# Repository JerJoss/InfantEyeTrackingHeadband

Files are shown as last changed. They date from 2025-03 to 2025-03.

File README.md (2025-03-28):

While most studies analyzing infant visual attention use methods varying from annotations of videos from head-mounted cameras, to fixed screen-based eye-tracking setups, increasing interest has been shown towards solutions that would pair the precision of eye-tracking with the free mobility offered by video annotation. This would allow infant research to gather high-quality visual attention data in naturalistic situations, which might yield results more representative of real-world infant environments. For this purpose, various forms of portable eye-tracking devices have been developed and used to study infant cognition, along with frequently time-consuming infant-adapted calibration procedures. Recently, the advent of calibration-free lightweight wearable eye-tracking systems developed by Pupil Labs© is offering new and simpler ways to study infant visual attention with the advantages of deep-learning calibration and miniaturization. However, despite a wide variety of wearing accessories being offered by the company, no suitable option currently exists for infants younger than 2 years old. In this paper, instructions will be provided to build a new wearing accessory for Pupil Labs’ Neon eye-tracking module adapted to 3 to 24 months-old infants, along with usage instructions.

Keywords—infant research, eye-tracking, Pupil Labs, Neon, calibration-free eye-tracking

<p>Video demonstrations:<br>
https://youtu.be/ldanZW603Fs - https://youtu.be/75sW56sUcog - https://youtu.be/vj5wvd1JuIk - https://youtu.be/4lynIBO4ydA</p>
<p>DISCLAIMER:<br>
These videos are intended solely for academic and research purposes. All content herein is shared in the context of scholarly inquiry and is not to be copied, distributed, or used for any commercial or non-research-related purpose. Unauthorized use, reproduction, or dissemination of this material is strictly prohibited.</p>

<p>Mail:<br>
jeremie.josse@univ-grenoble-alpes.fr<br></p>

<p>Files:<br>
Infant headband for Pupil Labs' Neon eyetracker — Instructions and method.pdf — Jérémie Josse (1)<br>
Custom_Neon_Module_receptacle.STL — 3D modelling by Eric Guinet (1) and Guillaume Bonnet<br>
<br>
(1) Laboratoire de Psychologie et Neuro-Cognition - UMR 5105 CNRS</p>

Thank you to Pupil Labs© for their willingness to be open source and their kind permission to make this custom use of their product public.

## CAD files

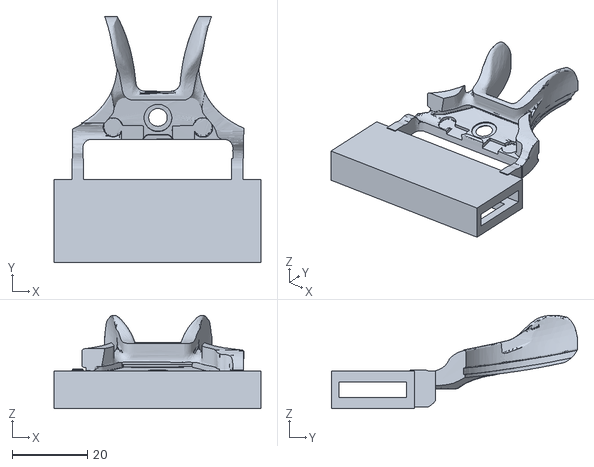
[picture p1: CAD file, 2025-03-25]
Custom_Neon_Module_receptacle.STL
55.0 x 65.4 x 24.7

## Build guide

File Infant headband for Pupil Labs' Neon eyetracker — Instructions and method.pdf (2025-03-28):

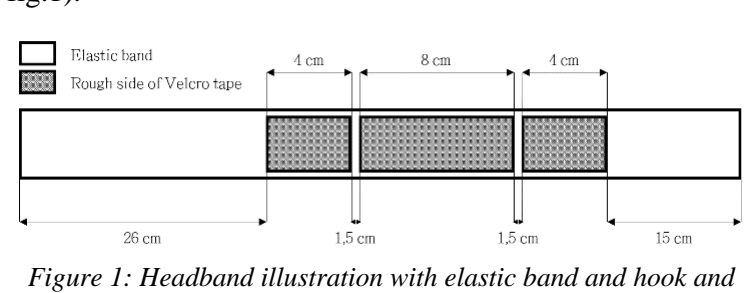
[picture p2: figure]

1 - https://github.com/JerJoss/InfantEyeTrackingHeadband/blob/main/Custom_Neon_Module_receptacle.STL 2 - https://github.com/pupil-labs/neon-geometry
3 - https://pupil-labs.com/products/neon/shop#bare-metal

# Using Pupil Labs’ Neon eye-tracking module for infants aged 3 to 24 months

Josse, Jérémie
BabyLab – Laboratory of Psychology and NeuroCognition
Grenoble Alpes University
Grenoble, France
jeremie.josse@univ-grenoble-alpes.fr

Abstract—While most studies analyzing infant visual attention use methods varying from annotations of videos from head-mounted cameras [1], [2], [4], [5] to fixed screen-based eye-tracking setups [6], [7], [8], [9], [10], increasing interest has been shown towards solutions that would pair the precision of eye-tracking with the free mobility offered by video annotation. This would allow infant research to gather high-quality visual attention data in naturalistic situations, which might yield results more representative of real-world infant environments [11]. For this purpose, various forms of portable eye-tracking devices have been developed and used to study infant cognition [3], [12], [13], [14], along with frequently time-consuming infant-adapted calibration procedures. Recently, the advent of calibration-free lightweight wearable eye-tracking systems developed by Pupil Labs© is offering new and simpler ways to study infant visual attention with the advantages of deep-learning calibration and miniaturization. However, despite a wide variety of wearing accessories being offered by the company, no suitable option currently exists for infants younger than 2 years old. In this paper, instructions will be provided to build a new wearing accessory for Pupil Labs’ Neon eye-tracking module adapted to 3 to 24 months-old infants, along with usage instructions.

Keywords—infant research, eye-tracking, Pupil Labs, Neon, calibration-free eye-tracking

I. INTRODUCTION
This document provides a series of instructions on how to make and use an accessory meant to facilitate the usage of Pupil Labs’ Neon eye-tracking module with infants aged 3 to 24 months. This eye-tracking module is particularly useful in the context of infant development research, as it is lightweight and miniaturised, and uses a deep-learning powered calibration which automatically adapts to its user — avoiding time-consuming calibration processes which might be difficult for infants to complete. In the initial phases of our experimentation with this tool, we tested various ways of using Pupil Labs’ official child-adapted frames designed for children aged 2 and older. However, due to their size and shape, we were not successful in adapting these to infant users. This led to the development of a new wearing accessory aimed towards infant wearers, which we have successfully been using to gather eye-tracking data from infants aged 3 to 24 months. We currently have an acceptance rate of 74% (n=70, aged 3 to 12m) using this tool in laboratory conditions, and 94% (n=18, aged 4 to 14m) in nurseries. Among the acceptance group, 39% have been excluded from our study due to experimental error (i.e. badly positioned module resulting in low-quality calibration, unplanned distraction in infant’s environment etc). In our whole sample of infants tested, 56% are currently included.

II. MAKING THE ACCESSORY

A. Materials
- A wide flat elastic band.
Here we used a 40mm-wide elastic band for sewing, generally used for tightening waistbands.
- Adhesive hook and loop (Velcro) strip tape.
35mm-wide.
- A plastic adjustment buckle.
- A 3D printed receptacle for the Neon eye-tracking module¹
, adapted from Pupil Labs’ open source “Just act natural” frame geometry²
- A piece of thick and soft fabric to smooth out the plastic edges.
- Pupil Labs’ Bare metal bundle: Neon eye-tracking module + Nest PCB + Android device³
B. Assembly
Cut a 60cm-long piece of the elastic band and sew 3 pieces of the rough (hook) side of the hook and loop strip tape (see fig.1).

Insert both edges of the elastic band in the adjustment buckle and sew one of the edges in a closed loop.

Cut a thin strip of the adhesive hook and loop tape, stick both sides together and form a loop around the side of the buckle. This will be used to assure the Neon eye-tracking module’s wire remains towards the back of the infant’s head so as not to distract them.

Figure 1: Headband illustration with elastic band and hook and loop strip tape dimensions.

Video demonstrations:
https://youtu.be/ldanZW603Fs - https://youtu.be/75sW56sUcog - https://youtu.be/vj5wvd1JuIk - https://youtu.be/4lynIBO4ydA

DISCLAIMER: These videos are intended solely for academic and research purposes. All content herein is shared in the context of scholarly inquiry and is not to be copied, distributed, or used for any commercial or non-research-related purpose. Unauthorized use, reproduction, or dissemination of this material is strictly prohibited.

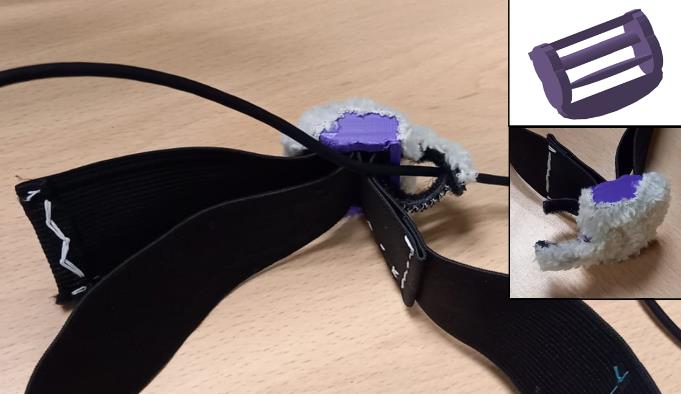
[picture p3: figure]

Glue a piece of the thick soft fabric over the buckle and the wire loop. This will make these surfaces softer in case of contact with the infant’s skin, and will decrease other problems such as the plastic or the loop getting caught in the fabric of the parents’ clothing when the infant sit on the parent’s lap (see fig.2).

Glue a piece of the thick soft fabric on the upper front section of the 3D printed module receptacle, along with some optional decorations. And glue a piece of the soft (loop) side of the hook and loop strip tape on the upper back section of the receptacle.

Screw the nest PCB inside the receptacle. Optionally, strengthen the base of the wire with a heat-shrink sleeve and small wire. This was added after an infant pulled on the wire, breaking the soldering connecting it to the nest PCB (see fig.3).

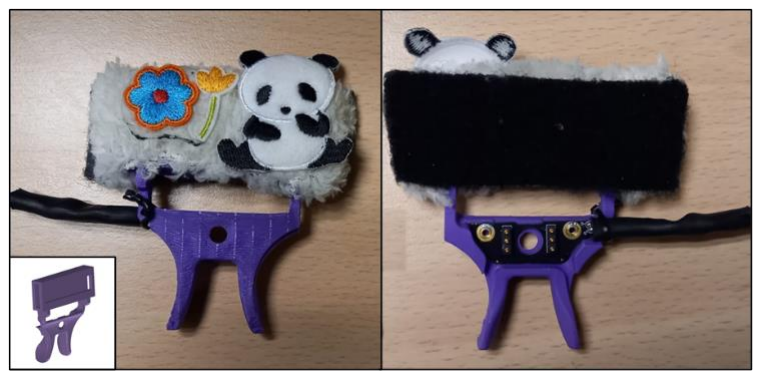
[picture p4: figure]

Screw the Neon eye-tracking module on the nest PCB and into the 3D-printed receptacle (see fig.4).

The final result should look like figure 5, with the receptacle fixed to the front of the headband using the hook and loop surfaces, and the wire going through the back loop.

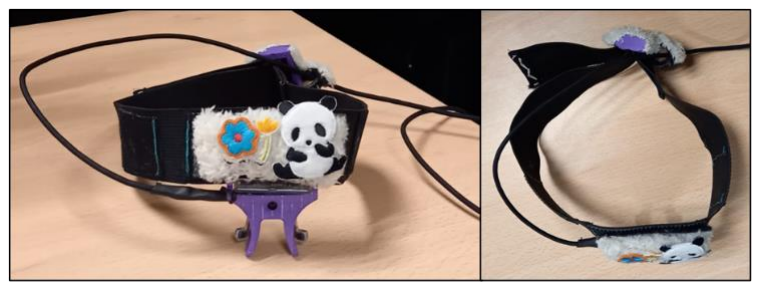
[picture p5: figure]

III. PROCEDURE
During our studies, the infant is seated on their parent’s lap, facing the experimenter. The infant is given a plush-toy meant to reassure and to distract its attention while the experimenter fits the headband and the eye-tracking module on its head. If possible, a second experimenter is present to play with the infant during the procedure.

After a short moment of playing and engaging with the infant, the first experiment takes the headband without the eye-tracking module, and approximately adjusts its circumference to be slightly wider than the infant’s head’s. At this stage, if the infant is showing more curiosity towards the headband than towards the plush-toy, it is encouraged to manipulate and familiarize itself with it. The experimenter then carefully slips the headband on the infant’s head, with the buckle to the back of the head and the rough (hook) side of the hook and loop strip tape to the front. The headband should run through the middle of the infant’s forehead. Ideally, any adjustments to its position should be done at this point while the eye-tracking module is not yet attached. If necessary, the experimenter then tightens the headband by pulling on the elastic band extending out of the buckle. Playing and engaging with the infant then continues until it seems comfortable wearing the headband.

The next step will to be to attach the eye-tracking module to the infant’s headband. Before starting, the eye-tracking module should be connected to the Android device and have been detected by the Neon Companion App. Inside the app, enable the sensor module camera view and position the Android device in a location that will be visually accessible while attaching the eye-tracking module to the infant’s headband (i.e. the parent’s chair’s armrest). Lastly, open the small loop next to the buckle and close it around the eye-tracking module’s wire, leaving just the right length for the module to reach the infant’s forehead. This will ensure that the wire won’t disturb the infant, or distract him by entering in its field of vision.

At this point, the eye-tracking module should be held above the infant’s head. The main or the second experimenter should then attempt to catch the infant’s attention. Whenever the infant’s head appears to be still, the

Figure 2: Picture of the buckle at the back of the headband.

Figure 3: Picture of the 3D-printed eye-tracking module receptacle, to be attached to the front of the headband using Velcro, along with a nest PCB.

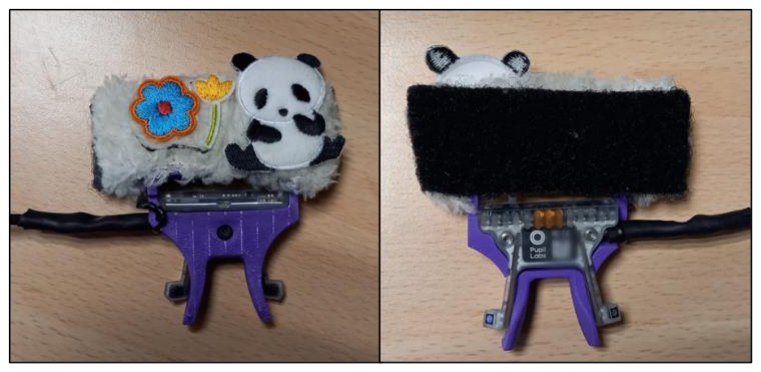
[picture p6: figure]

Figure 4: Picture of the 3D-printed eye-tracking module receptacle, to be attached to the front of the headband using Velcro, along with a Neon eye-tracking module.

Figure 5: Picture of the fully assembled headband.

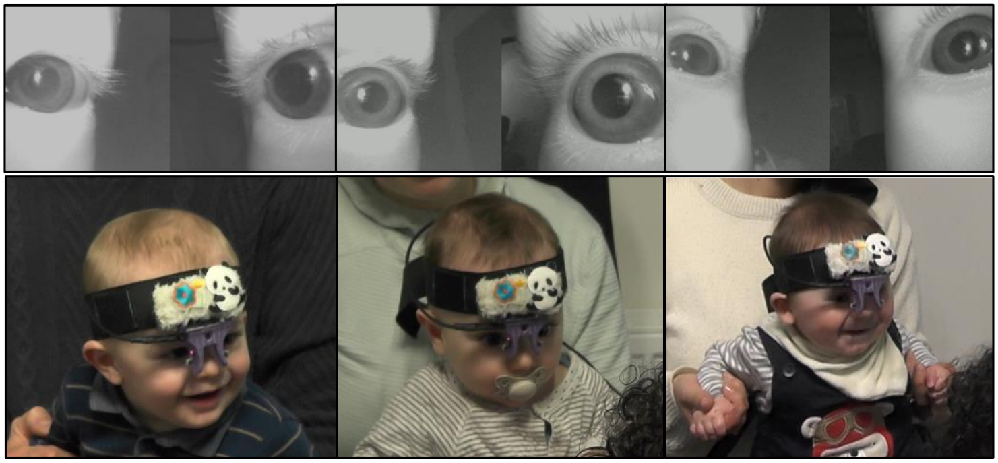
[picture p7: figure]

main experimenter attaches the eye-tracking module receptacle to the hook and loop surface on the headband. The sensor module camera view from the Neon Companion App should be visible during this process, and be used as a positioning guide for the experimenter. Once positioned, both eyes should be visible in the feedback (see fig.6). Ideally, the eyes should be well centered along the vertical axis of the visual feedback (as in the left and central examples of fig.6). In the correct position, the module receptacle nose pads should hover above the nose.

Once the position is correct, the recording can be started from the Neon Companion App.

IV. LIMITATIONS

A. Module positioning
One of the main challenges of this approach is getting the module to be positioned correctly. The reason behind the 2-step approach (first fitting the empty headband, then attaching the module), was that it greatly increased the acceptance rate with infants compared to our initial attempts with the module pre-attached to the headband. It does however have the downside of requiring a certain amount training before the experimenter can correctly position the module in most trials. In most cases, if the module positioning takes a bit of time, or is attempted more than once or twice, the infant will get distraught and refuse wearing the module altogether. A second version of the headband meant to simplify this process is currently being developed.
B. Infant reactions
During the recording, some infants will also attempt to touch the module, either to remove it or from simple curiosity. If the action seems to stem from simple curiosity, and the infant does not seem upset, the experimenter might gently guide the infant’s hand away from the module. Occasionally, parents also will also spontaneously grab their infant’s hands to prevent them from moving the module (see fig.6, right example).

However, if the infant does seem upset while attempting to remove the module, the experimenter helps to remove it and stops the recording.

C. Infant movements
During the recording, the infant might make sudden movements that, though unrelated to the module, may vertically shift the position of the headband and the module. This might occur if, for instance, the child leans backwards and the buckle gets pushed against the parent’s clothing. In these cases, the infant will often become bothered by the module’s movement, and the calibration will no longer be valid. In this case, the experimenter removes the headband and ends the recording.
D. Data accuracy
So far, this headband system is the best and only way we have found to use Pupil Labs’ Neon eye-tracker with infants. However, the headband does not precisely reproduce the optimal module position relative to the user’s eyes that actual Pupil Labs’ frames implement. Therefore, though we have been able to extract analyzable gaze data with this method, the accuracy of the data is somewhat varying and dependent the precision of each particular module positioning. We have particularly noticed what seems to be a lateral shift occasionally affect the gaze points. This entails that each recording needs to be rated for accuracy and included or excluded on that basis. In the study for which this method was developed, a subjective rating of each main camera and sensor module videos was used to decide whether the module

Figure 6: Below: Infants sitting on their parent’s lap, wearing a Pupil Labs’ Neon eye-tracking module attached to a headband during a study. Ages from left to right: 9 months, 9 months, 6 months. Above: visual feedback provided live from the sensor module camera view via the Neon Companion App.

was sufficiently well-positioned for the data to be included. However, any future studies should ideally include a more robust calibration confirmation process and gaze shift measurement.

ACKNOWLEDGMENT
We thank E. Guinet and G. Bonnet for the 3D modelling and printing; O. Astic and F. Gimbert for their participation in data-gathering with this tool; D. Meary for his helpful input and valuable help during development and testing; M. Fort, J. Birules, O.Pascalis and L.Goupil for their help, involvement and encouragement; the Domus platform for their lending of Pupil Labs’ Neon eye-tracker; Pupil Labs© for their willingness to be open source and their kind permission to make this custom use of their product public; R. Druilhe for his valuable advice in how best to share this method; the three parents who gave their permission for videos and pictures of their infants to be used for this demonstration; and we thank all of our participants.

REFERENCES

[1] N. A. Sugden and M. C. Moulson, ‘The infant’s face diet: Data on 3-month-old infant-perspective experience with faces video-recorded in their typical, daily environment’, Data Brief, vol. 29, p. 105070, Apr. 2020, doi: 10.1016/j.dib.2019.105070.
[2] C. Schmitow, G. Stenberg, A. Billard, and C. von Hofsten, ‘Using a head-mounted camera to infer attention direction’, Int. J. Behav. Dev., vol. 37, no. 5, pp. 468–474, 2013, doi: 10.1177/0165025413495749.
[3] J. M. Franchak, K. S. Kretch, K. C. Soska, and K. E. Adolph, ‘Head-Mounted Eye Tracking: A New Method to Describe Infant Looking’, Child Dev., vol. 82, no. 6, pp. 1738–1750, 2011, doi: 10.1111/j.1467-8624.2011.01670.x.
[4] R. N. Aslin, ‘How Infants View Natural Scenes Gathered From a Head-Mounted Camera’, Optom. Vis. Sci., vol. 86, no. 6, p. 561, Jun. 2009, doi: 10.1097/OPX.0b013e3181a76e96.
[5] L. B. Smith, Yu ,Chen, Yoshida ,Hanako, and C. M. and Fausey, ‘Contributions of Head-Mounted Cameras to Studying the Visual

Environments of Infants and Young Children’, J. Cogn. Dev., vol. 16, no. 3, pp. 407–419, May 2015, doi: 10.1080/15248372.2014.933430.
[6] D. J. Lewkowicz and A. M. Hansen-Tift, ‘Infants deploy selective attention to the mouth of a talking face when learning speech’, Proc. Natl. Acad. Sci. U. S. A., vol. 109, no. 5, pp. 1431–1436, Jan. 2012, doi: 10.1073/PNAS.1114783109.
[7] I. Lozano et al., ‘Changes in selective attention to articulating mouth across infancy: Sex differences and associations with language outcomes’, Infancy, vol. 27, no. 6, pp. 1132–1153, 2022, doi: 10.1111/infa.12496.
[8] E. Morin-Lessard, D. Poulin-Dubois, N. Segalowitz, and K. Byers-Heinlein, ‘Selective attention to the mouth of talking faces in monolinguals and bilinguals aged 5 months to 5 years’, Dev. Psychol., vol. 55, no. 8, pp. 1640–1655, 2019, doi: 10.1037/dev0000750.
[9] C. Alviar, M. Sahoo, L. A. Edwards, W. Jones, A. Klin, and M. Lense, ‘Infant-directed song potentiates infants’ selective attention to adults’ mouths over the first year of life’, Dev. Sci., vol. 26, no. 5, p. e13359, Sep. 2023, doi: 10.1111/DESC.13359.
[10] E. J. Tenenbaum, R. J. Shah, D. M. Sobel, B. F. Malle, and J. L. Morgan, ‘Increased Focus on the Mouth Among Infants in the First Year of Life: A Longitudinal Eye-Tracking Study’, Infancy, vol. 18, no. 4, pp. 534–553, 2013, doi: 10.1111/j.1532-7078.2012.00135.x.
[11] J. Birulés, L. Goupil, J. Josse, and M. Fort, ‘The Role of Talking Faces in Infant Language Learning: Mind the Gap between Screen-Based Settings and Real-Life Communicative Interactions’, Brain Sci., vol. 13, no. 8, Art. no. 8, Aug. 2023, doi: 10.3390/brainsci13081167.
[12] D. H. Abney, S. H. Suanda, L. B. Smith, and C. Yu, ‘What are the building blocks of parent-infant coordinated attention in free-flowing interaction?’, Infancy Off. J. Int. Soc. Infant Stud., vol. 25, no. 6, pp. 871–887, Nov. 2020, doi: 10.1111/infa.12365.
[13] C. Suarez-Rivera, L. B. Smith, and C. Yu, ‘Multimodal parent behaviors within joint attention support sustained attention in infants’, Dev. Psychol., vol. 55, no. 1, pp. 96–109, Jan. 2019, doi: 10.1037/dev0000628.
[14] L. K. Slone et al., ‘Gaze in Action: Head-mounted Eye Tracking of Children’s Dynamic Visual Attention During Naturalistic Behavior’,
J. Vis. Exp. JoVE, no. 141, Nov. 2018, doi: 10.3791/58496.

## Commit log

2025-03-25 Added 3d model of Neon module receptacle
    A 3D model of a receptacle for the Neon eye-tracking module, adapted from Pupil Labs’ open source “Just act natural” frame geometry (https://github.com/pupil-labs/neon-geometry).
    [Neon_From_JAN_frame_reference.STL]
2025-03-25 Rename Neon_From_JAN_frame_reference.STL to Custom_Neon_Module_receptacle.STL
    name changed
    [Custom_Neon_Module_receptacle.STL]
2025-03-25 Instructions and method upload
    Infant headband for Pupil Labs' Neon eyetracker — Instructions and method upload
2025-03-25 Update Infant headband for Pupil Labs' Neon eyetracker — Instructions and method.pdf
